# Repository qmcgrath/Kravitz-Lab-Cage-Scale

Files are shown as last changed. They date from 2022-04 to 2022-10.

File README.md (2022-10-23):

# Kravitz-Lab-Cage-Scale
Quinlan McGrath, Robbie Schaefer, Lex Kravitz, Gunwoo Lee

  The use of food and water restriction, drugs, surgery, and disease models in live mouse studies require continuous monitoring of body weight to surveill mouse health and determine experiment endpoints. Resolution of weight fluctuation over time can offer researchers a more complete picture of mouse health. Traditional manual weighing induces stress in mice and disrupts circadian rhythms.Existing commercial and open source autonomous mouse weight systems are available. However, commercial systems are not cost effective, cannot be used in colonial housing cages, or required rFID tags. 
 
Accurate, non-invasive recording of mouse weight allows for increased volume of body weight data while decreasing animal stress and human interaction. The developed scale can be constructed for $150 and operates for ~3.5 days on one charge. It has a small footprint of 7.6x8.6x8 cm and can be used in singley housed mice in traditional vivarium cages without modification. An Hx711 and proximity sensor work in tandem to determine mouse weight readings. The scale is operates on open source arduino code and data is anlysised with provided python code. 
  
  It was demonstrated that the scale can acheived and estimation of mouse weight with an average of 1.55% error with 50% hourly resolution (22 instances). Hourly resolution can be increased to 100% at the expense of an increased average error of 1.66% (33 instances). Accuracy was determined via comparision of maunaul weighing and reported weights for the same hour. Twenty two instances were used. It was demonstrated that this scale has potential appications in circadian rhythm monitoring, energy expendature evaluation, and group housed mice.  
  
 Assemebly, hardware and software overviews, quick start instructions, and code documentation are available in the wiki. The Jupyter notebooks used for data anlysis are provided. 

A graphical overview of embedded logic is shown below. 

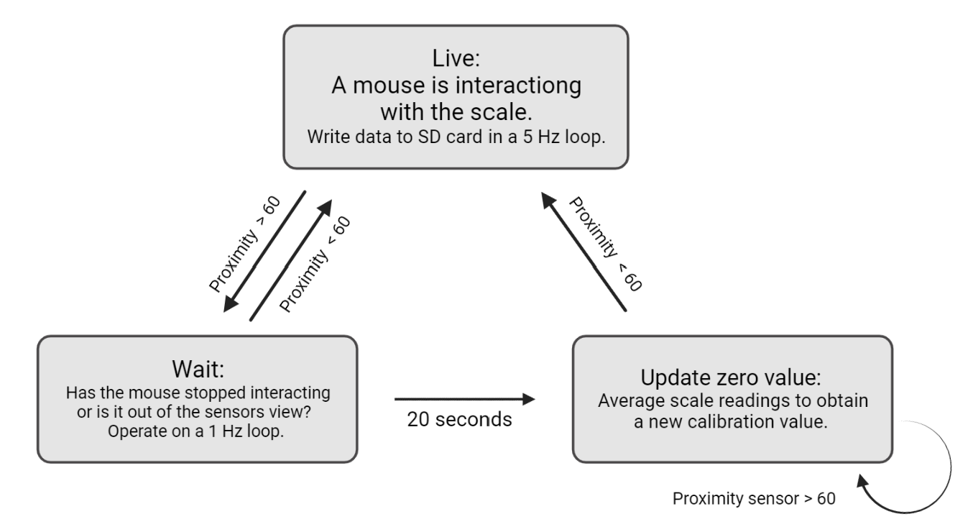
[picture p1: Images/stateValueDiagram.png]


## Results
Three scales (labeled A, B, C) were constructed and included in testing procedures. Individually house mice were monitored continuously for an average of 5 days. Manual weights were recorded at 33 instances.  

Code and data used are available above. The manual recorded weights are available in 'example data'.

Figure 1: Visualization of the basic scale operations. 

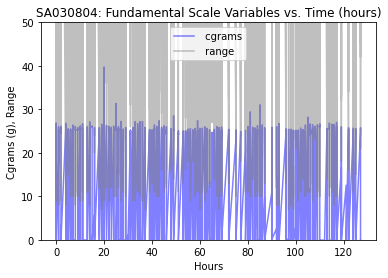
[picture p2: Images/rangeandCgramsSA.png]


Figure 2: Reported hourly weight (g) vs Time (hour)

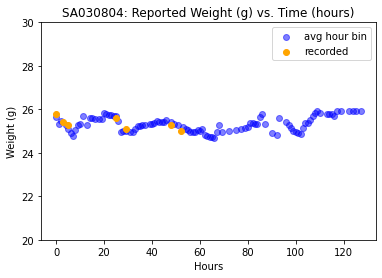
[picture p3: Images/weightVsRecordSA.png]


The methodology for calcuting the hourly weight from the scale data was simple. First, any report cgrams < 15 g were dropped, as it can be assumed these were recorded when the mouse was only partially on the scale. Next, the data was binned into hours and the median was found. Median weights were found to be more accurate than mode data. For further evaluation, a 'minimum number of cgram recordings per hour' was selected in which a reported weight could be deemed reliable or well informed. An array of minimum number counts, the resultant accuracy and resolution, and instances count (# of hours for which there was a manual weight available) are reported in Table 1. As shown, the average error is a minimum at a 150 instance thresehold. However, 100 data points was choosen as the optimal value as it has a higher resolution (nearly 50%) for minimum accuracy gain. Thus, it was determined that the scale can determine mouse weight with an accuracy of 1.55% with 50% resolution.

Figure 3: Weight error percent distribution. 

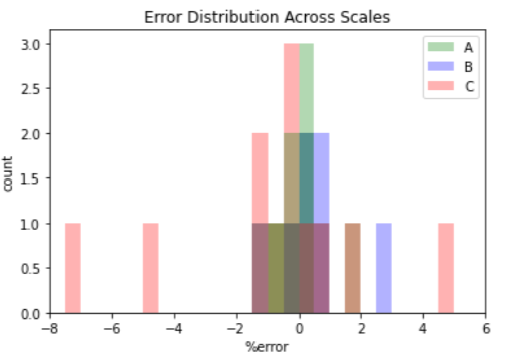
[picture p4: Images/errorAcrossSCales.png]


Table 1 was recreated for data in which hourly median weight was interpolated across hours with insufficient cgrams were reported. This increased resolution to 100%, will only minorly increasing overall error to 1.66%. 

However, it can be seen in the color coded histogram that not all scales performed equally. In fact, Table 3 demonstrates the distribution of error across the scales - with scale A outperforming the other two substaintially.

### Next Steps 
- More user friendly 3d design 
- improved calibration code

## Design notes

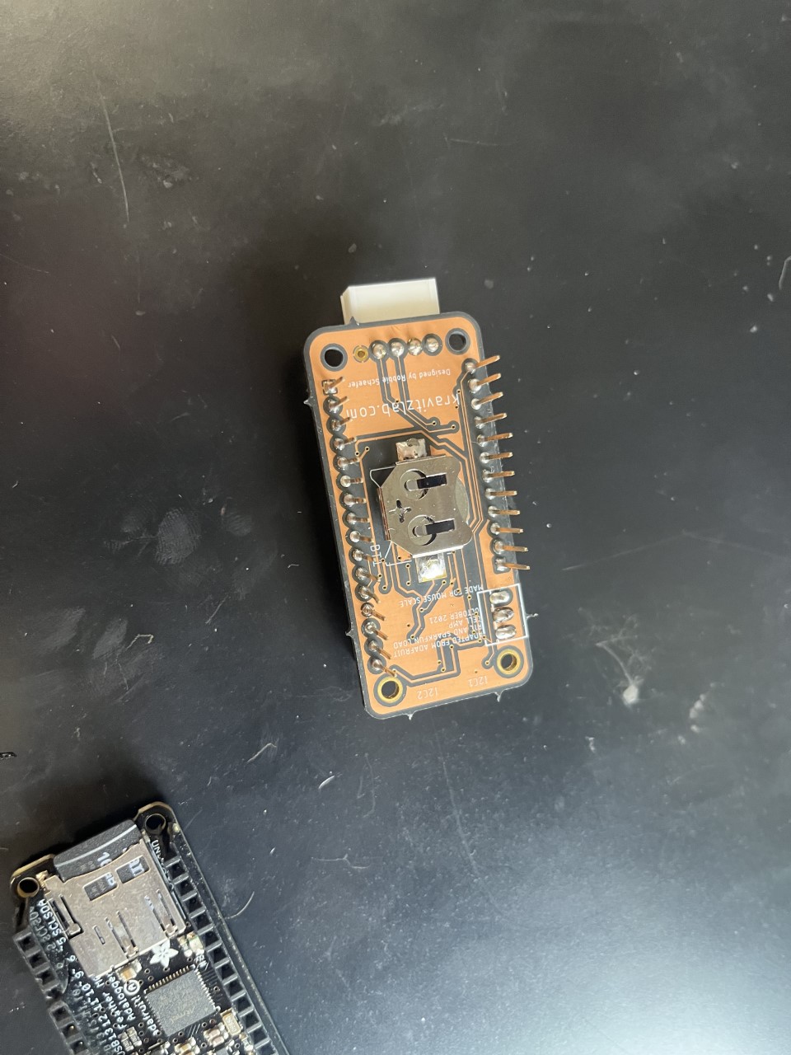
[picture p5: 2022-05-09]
Images/bottomBoard.jpg

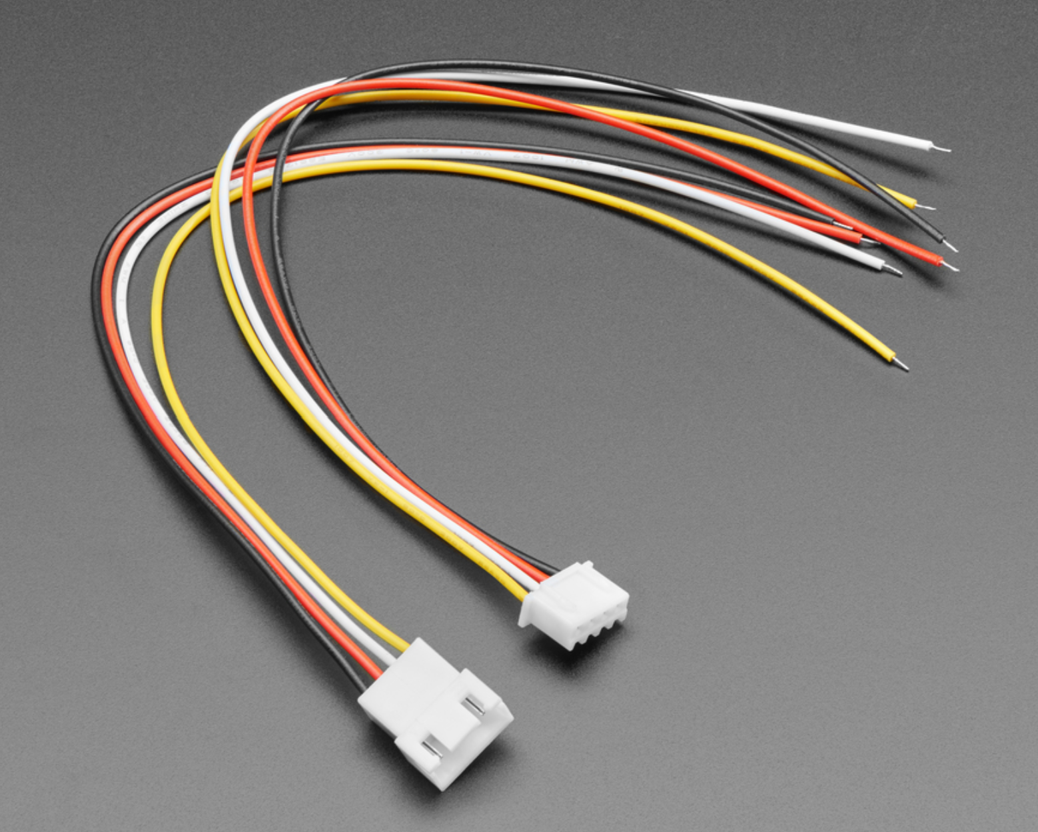
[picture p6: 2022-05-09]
Images/4pin.png

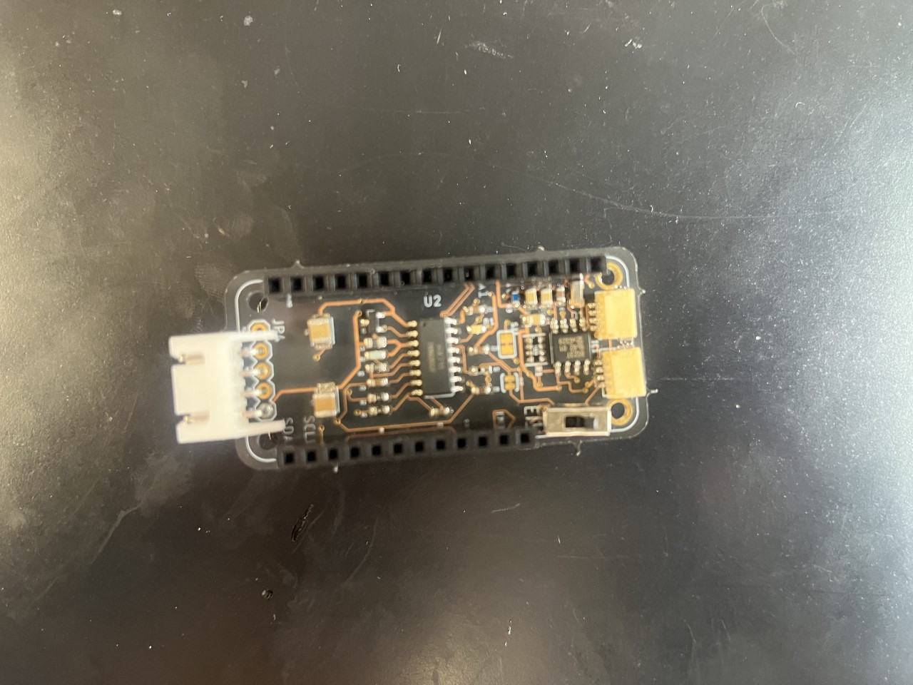
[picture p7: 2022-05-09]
Images/topFinishedBoard.jpg

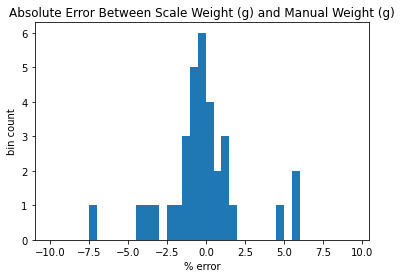
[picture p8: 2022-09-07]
Images/histrogamErrorNoScaleSEp.png

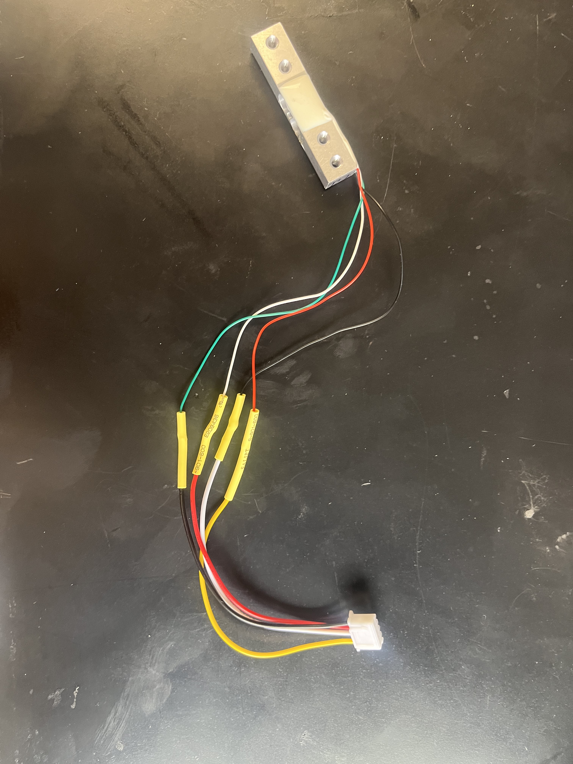
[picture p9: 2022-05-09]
Images/hx711Connections.jpeg

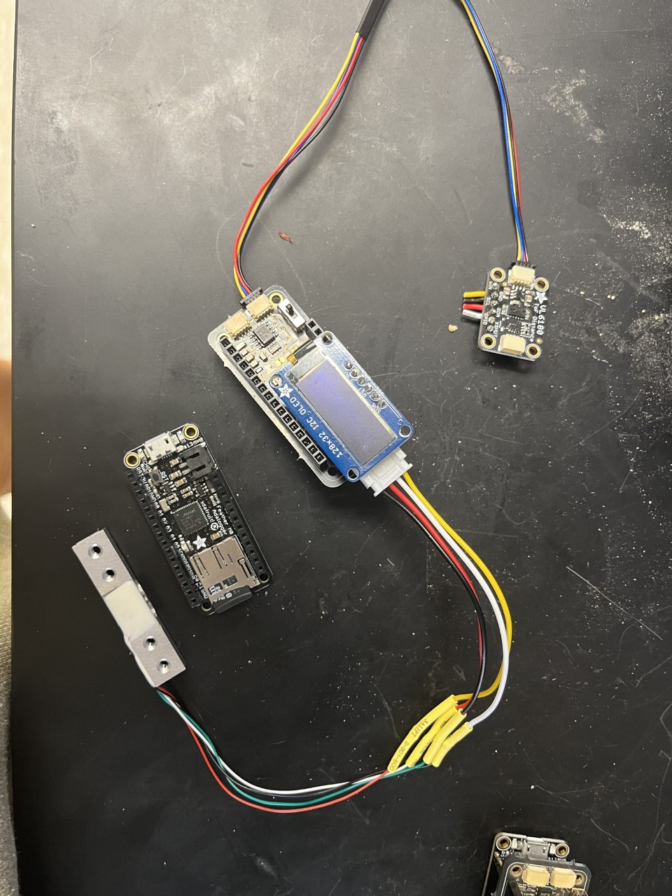
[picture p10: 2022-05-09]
Images/allGuts.jpg

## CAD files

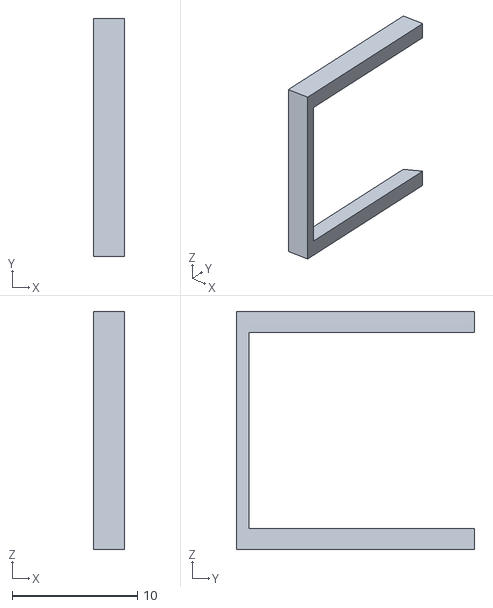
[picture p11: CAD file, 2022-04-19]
STlFiles/windowSlider(4-19).stl
2.50 x 19.0 x 19.0

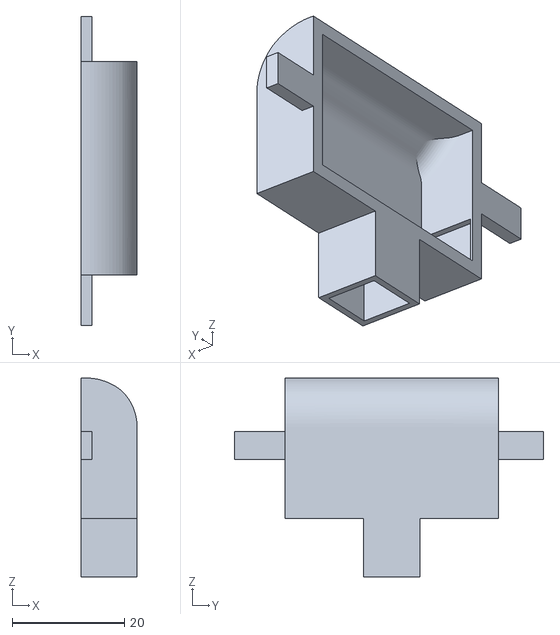
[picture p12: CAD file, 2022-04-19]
STlFiles/proxCover(4-19).stl
10.0 x 55.0 x 35.4

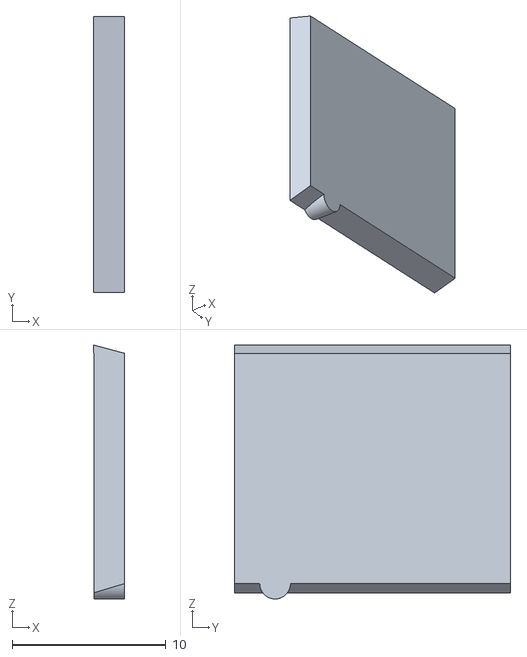
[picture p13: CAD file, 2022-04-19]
STlFiles/windowCover(4-19).stl
2.01 x 18.0 x 16.5

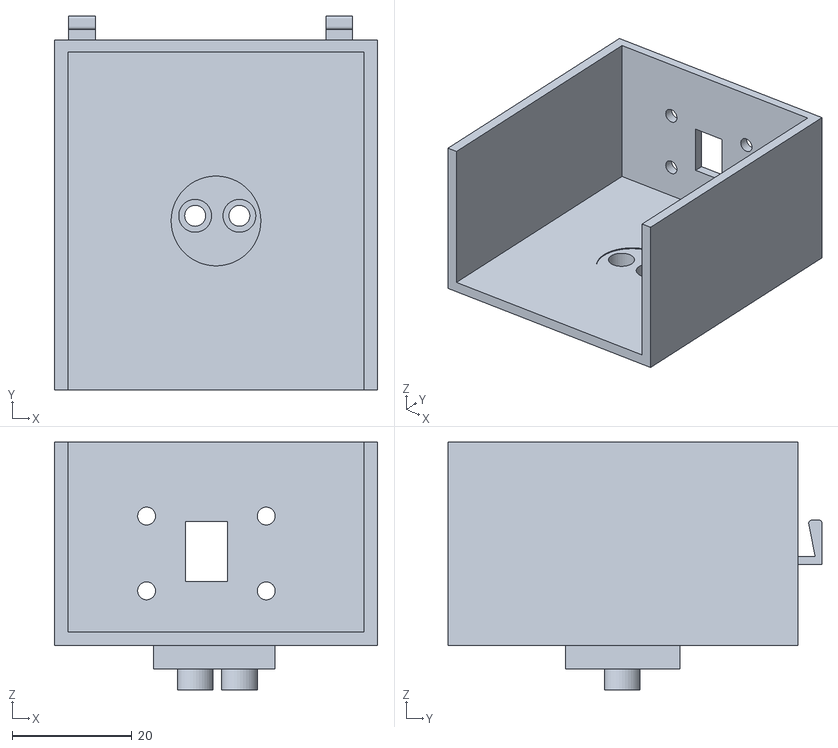
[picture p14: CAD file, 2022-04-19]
STlFiles/tubeWithGrasps(4-19).stl
54.0 x 62.5 x 41.4

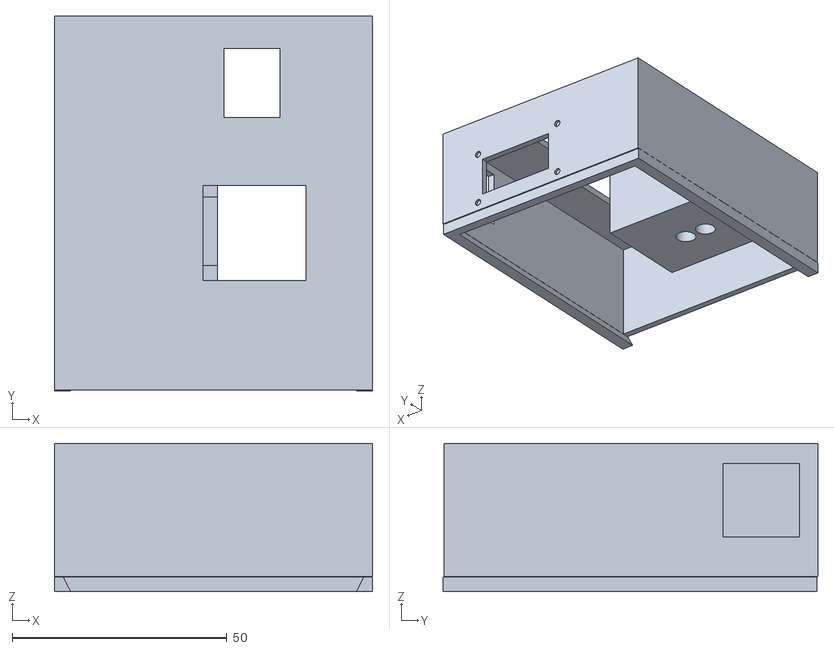
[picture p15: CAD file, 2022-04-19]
STlFiles/bottomWalls(4-19)(flash_window_only).stl
74.0 x 87.3 x 34.5

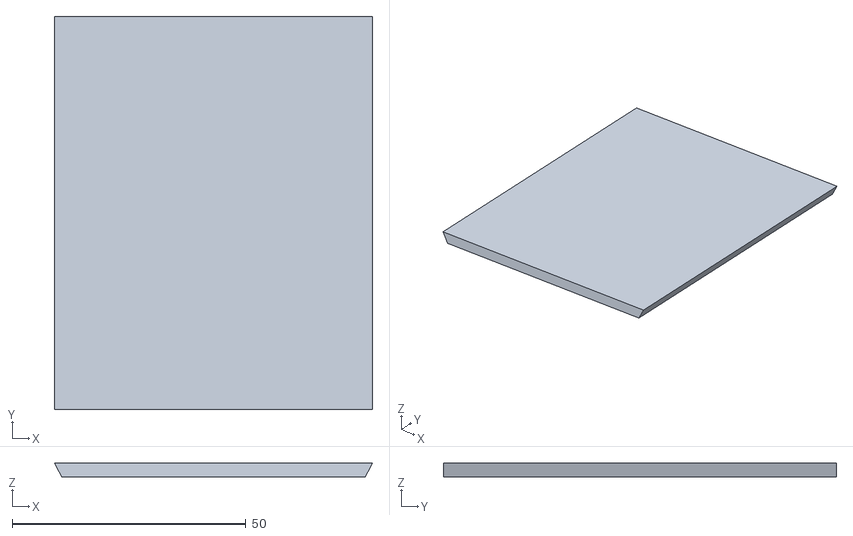
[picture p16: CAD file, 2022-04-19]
STlFiles/bottomLid4(4-19).stl
68.0 x 84.0 x 3.00

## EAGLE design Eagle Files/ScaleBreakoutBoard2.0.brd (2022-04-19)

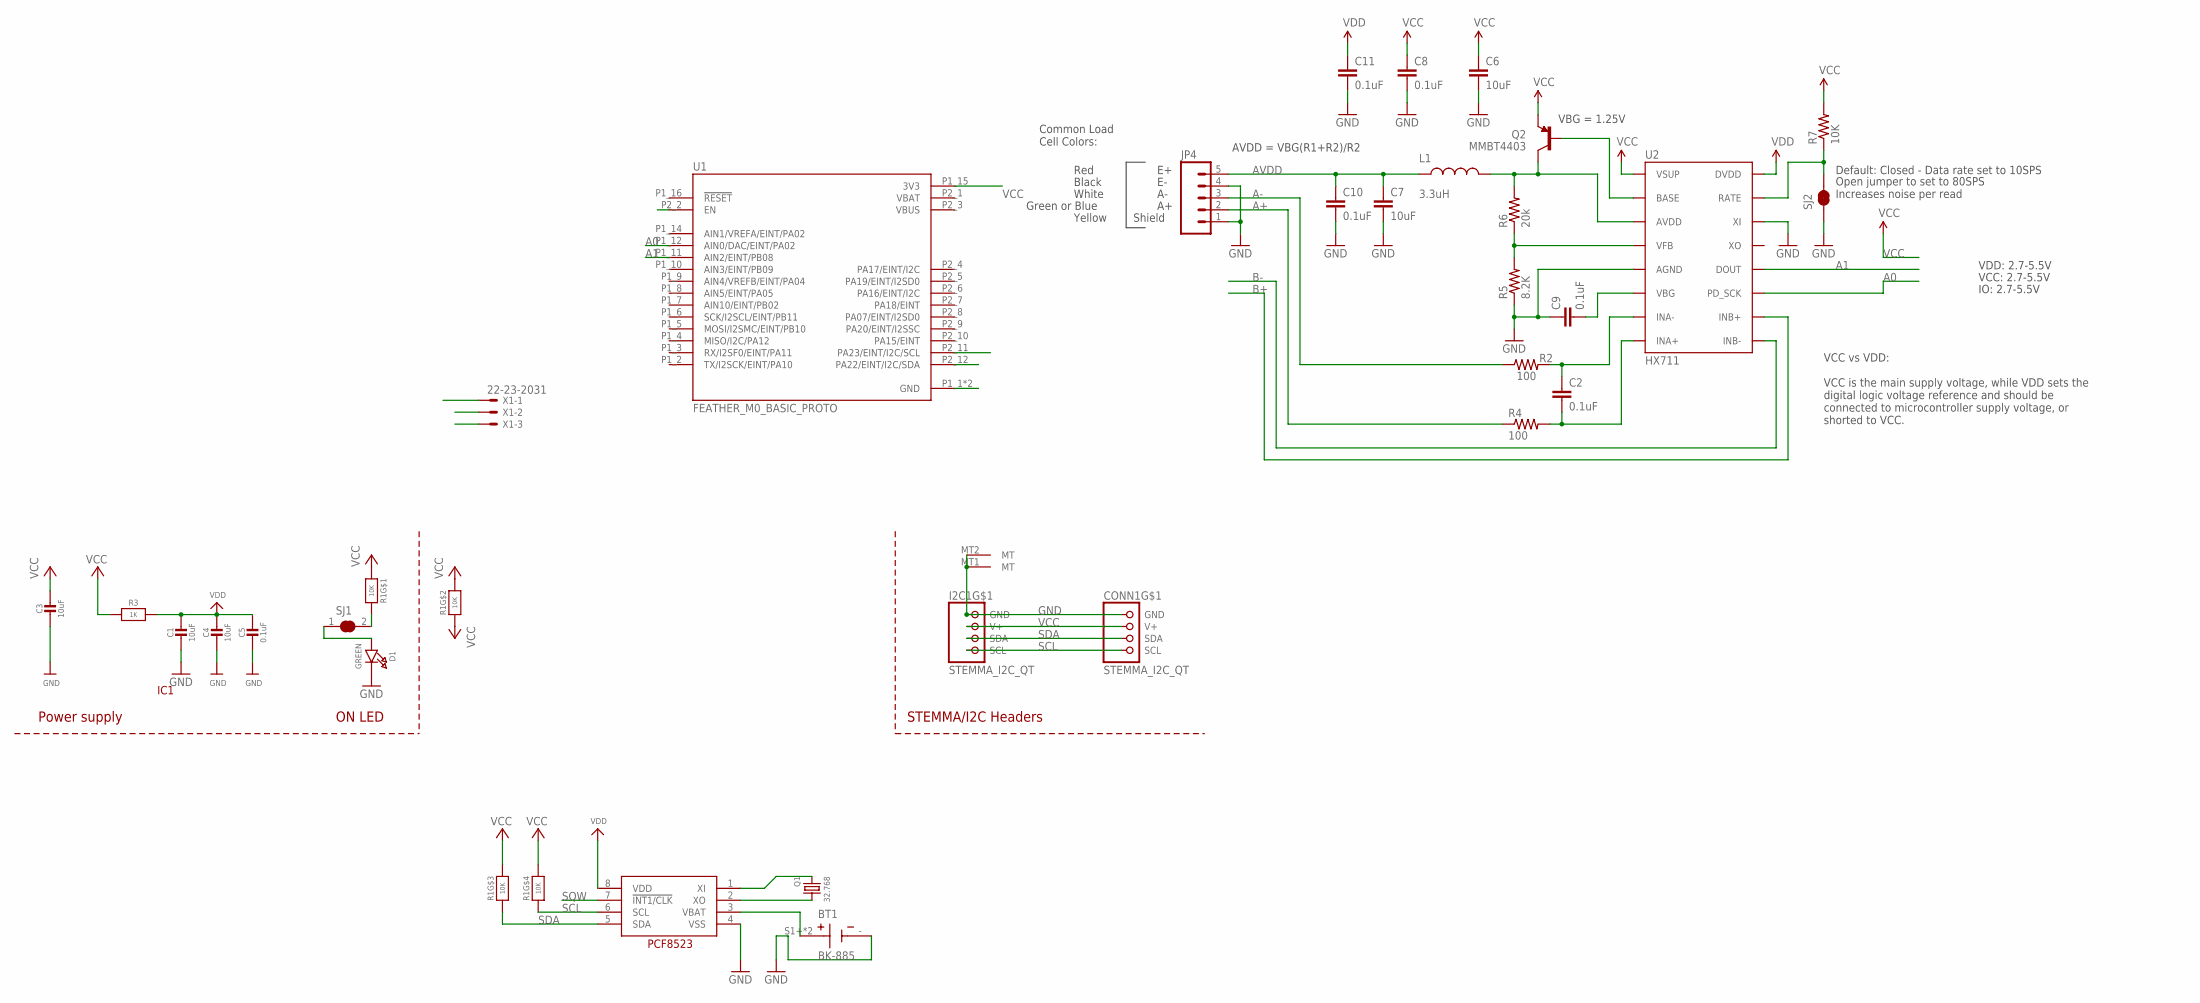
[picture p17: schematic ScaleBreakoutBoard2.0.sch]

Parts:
BT1: BK-885; BAT_BK-885
C1, C3, C4: 10uF; 0805-NO
C2, C8, C9, C10, C11: 0.1uF; 0603-CAP
C5: 0.1uF; 0603-NO
C6, C7: 10uF; 1210
CONN1: STEMMA_I2C_QT; JST_SH4
D1: GREEN; CHIPLED_0603_NOOUTLINE
I2C1: STEMMA_I2C_QT; JST_SH4
IC1: RTC_PCF8523T; SOIC8_150MIL
JP4: M05PTH; 1X05
L1: 3.3uH; 0805
Q1: 32.768; XTAL3215
Q2: MMBT4403; SOT23-3
R1: 10K; RESPACK_4X0603
R2, R4: 100; 0603-RES
R3: 1K; 0603-NO
R5: 8.2K; 0603-RES
R6: 20k; 0603-RES
R7: 10K; 0603-RES
SJ1: SOLDERJUMPER_CLOSED; SOLDERJUMPER_CLOSEDWIRE
SJ2: JUMPER-PAD-2-NC_BY_TRACE; PAD-JUMPER-2-NC_BY_TRACE_YES_SILK
U1: FEATHER_M0_BASIC_PROTO; MODULE_FEATHER_M0_BASIC_PROTO
U2: HX711; SO16
X1: 22-23-2031

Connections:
A0: U1.P1_12 (AIN0/DAC/EINT/PA02), U2.11 (PD_SCK)
A1: U1.P1_11 (AIN2/EINT/PB08), U2.12 (DOUT)
A+: JP4.2, R4.1
A-: JP4.3, R2.1
AVDD: C7.1, C10.1, JP4.5, L1.1
B+: U2.10 (INB+)
B-: U2.9 (INB-)
EN: U1.P2_2 (EN), X1.3
GND: BT1.-, C1.2, C3.2, C4.2, C5.2, C6.2, C7.2, C8.2, C9.1, C10.2, C11.2, CONN1.1 (GND), D1.C, I2C1.1 (GND), I2C1.MT1 (MT), I2C1.MT2 (MT), IC1.4 (VSS), JP4.1, JP4.4, R5.1, SJ2.1, U1.P1_1 (GND), U1.P1_13 (GND), U2.5 (AGND), U2.14 (XI), X1.1, X1.2
unnamed: R1.8 (2), SJ1.2
unnamed: Q2.1 (B), U2.2 (BASE)
unnamed: R7.1, SJ2.2, U2.15 (RATE)
unnamed: D1.A, SJ1.1
unnamed: L1.2, Q2.3 (C), R6.2, U2.3 (AVDD)
unnamed: R5.2, R6.1, U2.4 (VFB)
unnamed: C9.2, U2.6 (VBG)
unnamed: C2.1, R2.2, U2.7 (INA-)
unnamed: C2.2, R4.2, U2.8 (INA+)
unnamed: IC1.1 (XI), Q1.P$1 (1)
unnamed: IC1.2 (XO), Q1.P$2 (2)
SCL: CONN1.4 (SCL), I2C1.4 (SCL), IC1.6 (SCL), R1.4 (1), U1.P2_11 (PA23/EINT/I2C/SCL)
SDA: CONN1.3 (SDA), I2C1.3 (SDA), IC1.5 (SDA), R1.3 (1), U1.P2_12 (PA22/EINT/I2C/SDA)
SQW: IC1.7 (!INT1/CLK)
VBAT: U1.P2_1 (VBAT)
VBAT1: BT1.S1+ (+), BT1.S2+ (+), IC1.3 (VBAT)
VBUS: U1.P2_3 (VBUS)
VCC: C3.1, C6.1, C8.1, CONN1.2 (V+), I2C1.2 (V+), Q2.2 (E), R1.1, R1.2 (1), R1.5 (2), R1.6 (2), R1.7 (2), R3.1, R7.2, U1.P1_15 (3V3), U2.1 (VSUP)
VDD: C1.1, C4.1, C5.1, C11.1, IC1.8 (VDD), R3.2, U2.16 (DVDD)

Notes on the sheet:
STEMMA/I2C Headers
ON LED
Power supply
VCC: 2.7-5.5V
VBG = 1.25V
AVDD = VBG(R1+R2)/R2
Default: Closed - Data rate set to 10SPS
Open jumper to set to 80SPS Increases noise per read
Red
Black
White
Green or Blue
Common Load Cell Colors:
IO: 2.7-5.5V
Shield
Yellow
VDD: 2.7-5.5V
VCC vs VDD: VCC is the main supply voltage, while VDD sets the digital logic voltage reference and should be connected to microcontroller supply voltage, or shorted to VCC.

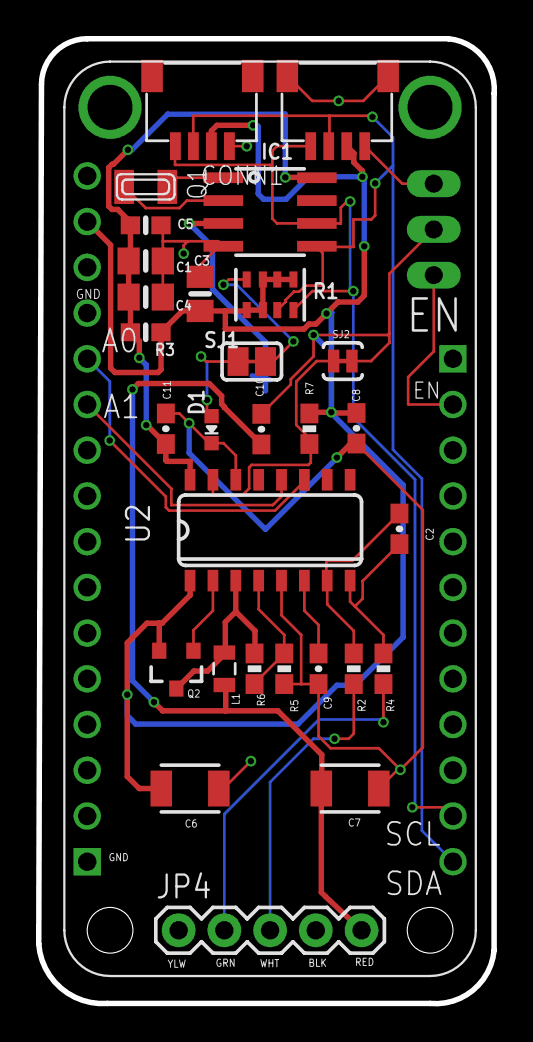
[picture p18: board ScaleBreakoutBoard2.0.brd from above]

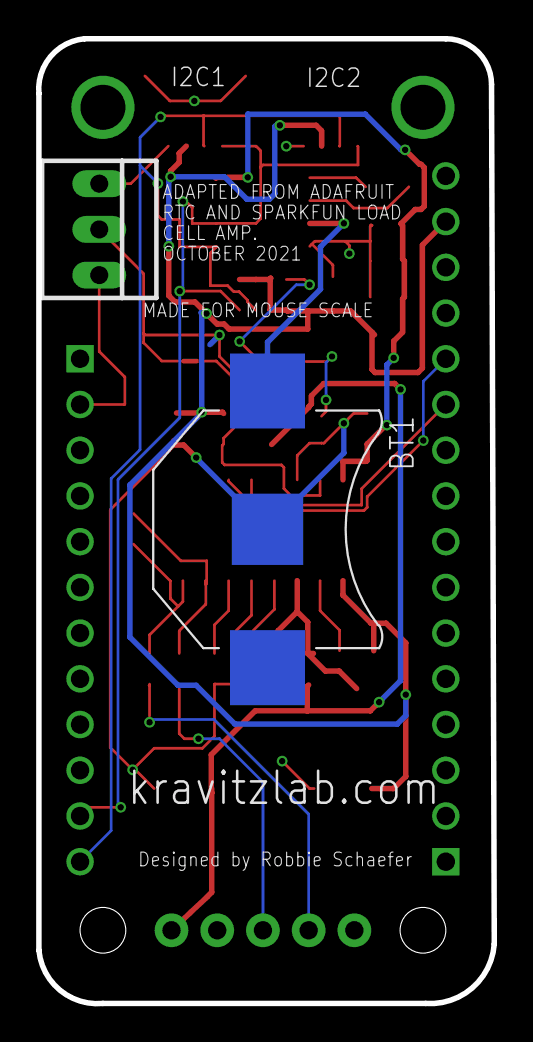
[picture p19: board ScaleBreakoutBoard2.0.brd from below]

Board: 2 copper layers, 25.3 x 53.6 mm, 32 parts (2 on the bottom side), 23 nets.

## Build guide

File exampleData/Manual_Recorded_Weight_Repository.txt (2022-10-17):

#recordedWeight demonstrates the manual weight taken in g
#placement in the cage = hour 0 
#SA030804
recordedWeight_SA030804 = [25.8, 25.43, 25.26, 25.6, 25.1, 25.3, 25]
hoursRecorded_SA030804 = [0 , 3, 5 ,25 ,29 ,48 ,52]

#SB030802
#recordedW_SB030802 = [29.13, 28.77, 28.47, 29.4, 28.7, 29, 29.1]
#hoursRecorded_SB030802 = [0 , 3, 5 ,25 ,29 ,48 ,52]

#SC030802
recordedW_SC030802 =[40.34, 40.0, 40.0, 41.0, 40.4, 39.7, 39.5]
hoursRecorded_SC030802 = [0 , 3, 5 ,25 ,29 ,48 ,52]

#SA032101
#recordedW_SA032101 = [29.5,29.29,29.29,29.2,29.39,29.56,29.63,29.19]
#hoursRecorded_SA032101 = [0 , 5, 24,29 ,48 ,53 ,72,77]

#SC032101
#recordedW_SC032101 = [26.72,26.74,27.13,27.11,27.13,27.13,27.4,27.03]
#hoursRecorded_SC032101  = [0 , 5, 24,29 ,48 ,53 ,72,77]

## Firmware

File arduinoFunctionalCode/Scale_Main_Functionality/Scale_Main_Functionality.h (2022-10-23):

#ifndef SCALE_MAIN_FUNCTIONALITY_h
#define SCALE_MAIN_FUNCTIONALITY_h

#include "Arduino.h"

#include <SPI.h>
#include <SD.h>
#include <Adafruit_GFX.h>

#include <Wire.h>
#include "Adafruit_VL6180X.h"

#include <unistd.h>

#include "HX711.h"
#include "RTClib.h"
#include <Adafruit_SSD1306.h>
#include <histogram.h>


#define DISGRND 6
#define DISPLAYPOWER 10
#define DISPLAYRESET 5

#define DOUT A1
#define CLK A0
#define VBATPIN A7

#define SCREEN_WIDTH 128 // OLED display width, in pixels
#define SCREEN_HEIGHT 32 // OLED display height, in pixels
#define OLED_RESET 5 // Reset pin # (or -1 if sharing Arduino reset pin)
#define SCREEN_ADDRESS 0x3C ///< See datasheet for Address; 0x3D for 128x64, 0x3C for 128x32

using namespace std;

void dateTime(uint16_t* date, uint16_t* time);

class Scale {

  public:
    Scale(String ver);
    String ver = "undef";
    String library_version = "undef";


    char scaleID = 'B'; /////// For the first run MANUALLY SET TO CHOOSEN LETTER ID
    
    //display
    Adafruit_SSD1306 display = Adafruit_SSD1306(SCREEN_WIDTH, SCREEN_HEIGHT, &Wire, OLED_RESET);

    //basic functions
    void Sense();
    void Tare();
    void autoCalibrate();
    void start_up_menu();
    void newTare();
    void startUp();
    void start_up_ScreenTwo();
    void noSettingsFile();

    //load cells
    HX711 scale;
    unsigned long mill = millis();
    int calibration_factor = 0;
    float outputValue;
    float grams;
    int taredCount = 0;

    bool calIndicator = false;

    float calibrateCell();
    int calStarter = 0;
    float calibrateBuffer[20];
    float calibrationAvg = 0;
    float totalCal = 0;
    int numInCal = 0;
    int timesCorrect = 0;


    unsigned long start_timer = 0;
    unsigned long taring_timer = 0;
    bool start_up = true;
    int proxLimitforMouseIn = 80;
    unsigned long delayTime = 1000;
    unsigned long tareWait = 30000;

    //proximity senor
    Adafruit_VL6180X vl = Adafruit_VL6180X();
    float lux = 0;
    uint8_t range = 0;
    unsigned long mouseHere_timer = 0;

    //moving avgerages
    void calcMovingAvg(float currentGram);
    float movingWeightAvg = 0;
    float currentGram = 0;
    float totalWeight = 0;
    float avgWeightBuffer[10];
    int numInAvgWeight = 0;

    void calcZeroAvg();
    float movingZeroAvg = 0;
    float totalZero = 0;
    float avgZeroBuffer[5];
    float movingZero;
    int numInAvgZero = 0;
    bool withinLimits = true;

    float cgrams = 0;

    float weightAfterCertainTime[2000];
    int weightVector = 0;


    void updateDisplay();

    //sd file
    File dataFile;               // Create file object
    char filename[15] ;          // Array for file name data logged to named in setup
    const int chipSelect = 4;
    void CreateDataFile();
    void writeHeader();
    void WriteToSD();
    void error(uint8_t errno);
    void getFilename(char *filename);
    unsigned long unixtime = 0;
    int SCL = 1;


    File calFile;
    char calFilename[13] =  "settingsCal.txt";


    float measuredvbat = 1.00;
    void ReadBatteryLevel();

    //rtc
    const byte seconds = 0;
    const byte minutes = 0;
    const byte hours = 16;
    const byte day = 15;
    const byte month = 6;
    const byte year = 15;
    bool calibrate = true;

    //for max hist
    float binVal = 10;
    float histToWrite = 0;
    void manageHist(float grams);

    bool mouseInHouse = false;

};

#endif

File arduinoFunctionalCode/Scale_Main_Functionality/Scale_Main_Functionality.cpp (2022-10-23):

#include "Scale_Main_Functionality.h"

RTC_PCF8523 rtc;
//for histogram

float bounds[400];
Histogram hist(400, bounds);

void dateTime(uint16_t* date, uint16_t* time) {
  DateTime now = rtc.now();
  // return date using FAT_DATE macro to format fields
  *date = FAT_DATE(now.year(), now.month(), now.day());

  // return time using FAT_TIME macro to format fields
  *time = FAT_TIME(now.hour(), now.minute(), now.second());
}

Scale::Scale(String ver) {
  library_version = ver;
}
/////////////////start UP
void Scale::startUp() {
  pinMode(13, OUTPUT);
  pinMode(8, OUTPUT);
  pinMode(DISGRND, OUTPUT);
  pinMode(DISPLAYPOWER, OUTPUT);
  digitalWrite(DISGRND, LOW);
  digitalWrite(DISPLAYPOWER, HIGH);

  if (!display.begin(SSD1306_SWITCHCAPVCC, SCREEN_ADDRESS)) {
    Serial.println("SSD1306 allocation failed");
  }

  //Start Serial port
  Serial.begin(9600);
  scale.begin(DOUT, CLK);
  scale.set_scale();

  rtc.begin();
  if (! rtc.isrunning()) {
    Serial.println("RTC is NOT running, let's set the time!");
    // When time needs to be set on a new device, or after a power loss, the
    // following line sets the RTC to the date & time this sketch was compiled
    rtc.adjust(DateTime(F(__DATE__), F(__TIME__)));
  }

  start_timer = millis();
  scale.tare();
  Serial.println("Adafruit VL6180x test!");
  if (! vl.begin()) {
    Serial.println("Failed to find sensor");
  }

  //get file id if it exists, if not will have to be set manually in h file. If settings differs from hfile, sd will overwrite her

  Serial.println("Sensor found!");
  Serial.println(scaleID);
  SdFile::dateTimeCallback(dateTime);
  Serial.println("creating datafile");
  CreateDataFile();

  display.clearDisplay();
  scale.tare();

  if (SD.exists(calFilename)) {
    calFile = SD.open("settings.txt");
    scaleID = calFile.read();
    calFile.close();

  }
  else {
    noSettingsFile();
  }

}



//must manually set scale id
void Scale::noSettingsFile() {
  float start_timer = millis();
  display.clearDisplay();
  display.setTextSize(1);      // Normal 1:1 pixel scale
  display.setTextColor(SSD1306_WHITE); // Draw white text
  display.setCursor(0, 0);     // Start at top-left corner

  display.println("NO SETTINGS FILE");
  display.println("Flash startup code");
  display.display();

  while (true) {
    Serial.println("no settings file");
  }

}



void Scale::start_up_menu() {
  float start_timer = millis();
  display.clearDisplay();
  display.setTextSize(1);      // Normal 1:1 pixel scale
  display.setTextColor(SSD1306_WHITE); // Draw white text
  display.setCursor(0, 0);     // Start at top-left corner

  display.println("Starting up");
  display.display();
  //wait x seconds for heavy press
  delay(4000);
  float starttime = millis();
  start_up_ScreenTwo();
}

void Scale::start_up_ScreenTwo() {
  // read in and set calibration factor from filename
  dataFile.close();

  // re-open the file for reading:
  calFile = SD.open(calFilename);
  int cal;
  if (calFile) {
    Serial.println(calFilename);

    // read from the file until there's nothing else in it:

    scaleID = calFile.read();
    cal = calFile.parseInt();
    Serial.print(cal);
    while (calFile.available()) {
      calFile.read();
    }

    calFile.close();
  }
  else {
    // if the file didn't open, print an error:
    Serial.println("error opening setting.txt");
  }

  Serial.println("id read from file:");
  Serial.println(scaleID);
 ///!!!!!!!!!!!!!!!
  calibration_factor = 3530 ;
  Serial.println("cal read from file:");
  Serial.println(calibration_factor);

  //write and open main file
  dataFile = SD.open(filename, FILE_WRITE);

  float start_timer = millis();

  display.clearDisplay();
  display.setTextSize(1);      // Normal 1:1 pixel scale
  display.setTextColor(SSD1306_WHITE); // Draw white text
  display.setCursor(0, 0);     // Start at top-left corner


  while (start_up ) {
    if ((millis() - start_timer) > 6000) start_up = false; //after 10 seconds of start up menu, start session
    display.setCursor(2, 2);
    display.println("Scale beginning!");
    display.setCursor(2, 11);
    display.println("filename:    ");
    display.setCursor(2, 20);
    display.println(filename);
    display.display();
  }
  display.clearDisplay();
  display.setCursor(2, 10);
  display.println("dont touch...taring");
  display.display();
  delay(3000);
  scale.tare();
  display.clearDisplay();
  Serial.println("end of startup");
}



////////////////menus and display functions


void Scale::updateDisplay() {
  Serial.println("in update display");
  display.clearDisplay();
  display.setTextSize(1);
  display.setCursor(0, 2);
  display.setTextColor(SSD1306_WHITE);
  display.print("grams: ");
  display.println(grams);
  display.print("Range: ");
  display.println(range);
  display.print("Avg Zero: ");
  display.println(movingZeroAvg );
  display.print("Cgrams: ");
  display.println(cgrams);
  display.display();
}



////////////file and SD functions
void Scale::error(uint8_t error) {
  display.clearDisplay();
  display.setTextSize(1);
  display.setCursor(0, 2);
  display.print("Check SD card");
  display.display();
}

void Scale::CreateDataFile() {
  SdFile::dateTimeCallback(dateTime);
  if (!SD.begin(chipSelect)) {
    Serial.println("Card failed, or not present");
    display.clearDisplay();
    display.setTextSize(1);
    display.setCursor(0, 2);
    display.setTextColor(SSD1306_WHITE);
    display.print("SD Card failed, or not present");
    while (1);
  }
  strcpy(filename, "________.CSV");  // placeholder filename
  Serial.println("entering get filename");
  getFilename(filename);
  Serial.println(filename);
  writeHeader();
}


void Scale::getFilename(char *filename) {

  DateTime now = rtc.now();
  filename[0] = 'S';
  filename[1] = scaleID;
  filename[2] = now.month() / 10 + '0';
  filename[3] = now.month() % 10 + '0';
  filename[4] = now.day() / 10 + '0';
  filename[5] = now.day() % 10 + '0';
  filename[8] = '.';
  filename[9] = 'C';
  filename[10] = 'S';
  filename[11] = 'V';

  for (uint8_t i = 0; i < 100; i++) {
    filename[6] = '0' + i / 10;
    filename[7] = '0' + i % 10;

    if (! SD.exists(filename)) {
      break;
    }
  }
  Serial.println(filename);
  return;
}

void Scale::writeHeader() {
  dataFile = SD.open(filename, FILE_WRITE);
  if ( ! dataFile ) {
    Serial.println("SD Create error");
    display.clearDisplay();
    display.setTextSize(1);
    display.setCursor(0, 2);
    display.setTextColor(SSD1306_WHITE);
    display.print("SD File Create Error");
    error(2);
  }
  dataFile.println("MM: DD: YYYY hh: mm: ss, Seconds, filename, calibration factor, output_value, lux, range, grams, tareCount, weightAvg, zeroAvg, cgrams, currentMaxHist, batteryLevel");
}

void Scale::WriteToSD() {
  DateTime now = rtc.now();
  dataFile.print(now.month());
  dataFile.print(" / ");
  dataFile.print(now.day());
  dataFile.print(" / ");
  dataFile.print(now.year());
  dataFile.print(" ");
  dataFile.print(now.hour());
  dataFile.print(": ");
  if (now.minute() < 10)
    dataFile.print('0');      // Trick to add leading zero for formatting
  dataFile.print(now.minute());
  dataFile.print(": ");
  if (now.second() < 10)
    dataFile.print('0');      // Trick to add leading zero for formatting
  dataFile.print(now.second());
  dataFile.print(", ");

  dataFile.print((millis() - start_timer) / 1000.0000);
  dataFile.print(", ");
  dataFile.print(filename);
  dataFile.print(", ");
  dataFile.print(calibration_factor);
  dataFile.print(", ");
  dataFile.print(outputValue);
  dataFile.print(", ");
  dataFile.print(lux);
  dataFile.print(", ");
  dataFile.print(range);
  dataFile.print(", ");
  dataFile.print(grams);
  dataFile.print(", ");
  dataFile.print(taredCount);
  dataFile.print(", ");
  dataFile.print(movingWeightAvg);
  dataFile.print(", ");
  dataFile.print(movingZeroAvg);
  dataFile.print(", ");
  dataFile.print(cgrams);
  dataFile.print(", ");
  dataFile.print(histToWrite);
  dataFile.print(", ");
  dataFile.println(measuredvbat);
  dataFile.flush();
}

void Scale::manageHist(float grams) {
  if ((grams >= 15) && (grams <= 40)) {
    hist.add(grams);
  }
  if (hist.count() >= 2000) {
    histToWrite = bounds[hist.findMax()];
    hist.clear();
  }
}

void Scale::Sense() {
  grams = (scale.get_units(5));
  if (grams < 0) {
    grams = 0;
  }
  Serial.print(scale.get_units(5));
  cgrams = grams - movingZeroAvg;
  Serial.print("grams = ");
  Serial.println(grams);

  outputValue = scale.read();
  Serial.print("failing at read scale");

  range = vl.readRange();
  lux =  vl.readLux(VL6180X_ALS_GAIN_5 );
  Serial.print("range = ");
  Serial.println(range);

  Serial.print("failing at range");
}

void Scale::Tare() {
  scale.tare();
  taredCount ++;
}
void Scale::calcMovingAvg(float currentGram) {
  if ( (currentGram >= 15) && (currentGram <= 40)) {
    avgWeightBuffer[numInAvgWeight ] = currentGram;
    if (numInAvgWeight != 0 && numInAvgWeight % 9 == 0) {
      for (int i = 0; i < 10; i++ ) {
        totalWeight += avgWeightBuffer[i];
      }

      movingWeightAvg =  (totalWeight) / numInAvgWeight;
      Serial.println(movingWeightAvg);
      numInAvgWeight = -1;
      totalWeight = 0;
    }
    numInAvgWeight++;
  }
}

void Scale::calcZeroAvg() {
  currentGram = scale.get_units(5);
  if (currentGram <= 15) {
    avgZeroBuffer[numInAvgZero] = currentGram;
    if (numInAvgZero != 0 && numInAvgZero % 4 == 0) {
      for (int i = 0; i < 5; i++ ) {
        totalZero += avgZeroBuffer[i];
      }
      movingZero =  totalZero / numInAvgZero;
      numInAvgZero = -1;
      totalZero = 0;
    }
    numInAvgZero++;
  }
  for (int i = 0; i < 5; i++ ) {
    if (abs( avgZeroBuffer[i] - movingZeroAvg) > .2) {
      withinLimits = false;
    }
  }
  //write to sd
  if (withinLimits) {
    Serial.println("passing within moving avg limits");
    movingZeroAvg = movingZero;
  }
  updateDisplay();
}



/////////check battery
void Scale::ReadBatteryLevel() {
  measuredvbat = analogRead(VBATPIN);
  measuredvbat *= 2;    // we divided by 2, so multiply back
  measuredvbat *= 3.3;  // Multiply by 3.3V, our reference voltage
  measuredvbat /= 1024; // convert to voltage
}

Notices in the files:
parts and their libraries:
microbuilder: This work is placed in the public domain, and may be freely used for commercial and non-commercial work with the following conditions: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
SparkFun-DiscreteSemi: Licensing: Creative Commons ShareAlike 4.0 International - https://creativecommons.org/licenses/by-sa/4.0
